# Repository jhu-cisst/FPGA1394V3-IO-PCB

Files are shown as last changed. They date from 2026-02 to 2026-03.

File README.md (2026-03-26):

# FPGA1394V3-IO-PCB

PCB design for I/O board used with [FPGA1394V3](https://github.com/jhu-cisst/FPGA1394V3), in KiCad format.

This board connects to the DF11 connector (J9) on FPGA1394V3, which provides +3.3V, GND and 4 I/O signals (MIO34-37) from the Zynq SoC PS, and makes protected versions of these signals available on a DB9F connector. Specifically, the +3.3V output has a 100 mA current limit and the I/O signals have 50 Ohm current-limiting resistors and a transorb (TVS diode) for protection.

This board is used in the [dVRK Si Controller](https://github.com/jhu-dvrk/dVRK-Si-Controller), starting with Rev 4 of the enclosure.

## DB9F Connector Pinout

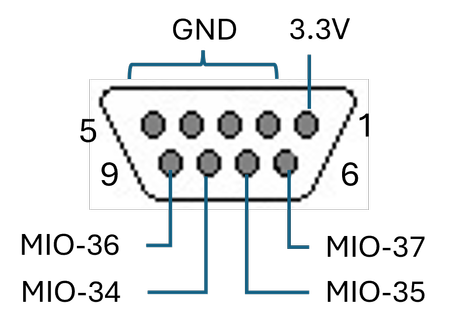
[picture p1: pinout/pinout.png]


## Files

* `dvrk-ios.kicad_pro`: KiCad project file
* `dvrk-ios.kicad_sch`: Schematics (KiCad format)
* `dvrk-ios.kicad_pcb`: PCB layout (KiCad format)
* `dvrk-ios-bom.xlsx`: Bill of Materials (Excel format)

## Subdirectories
(These are not required, since the symbols and footprints are already stored in the kicad_sch and kicad_pcb files)

* `3d`: 3D models of parts
* `DVRK.pretty`: Library of footprints (for PCB)
* `symbols`: Library of symbols (for schematics)

## Release Assets

* `dvrk-ios-schematics.pdf`: Schematics
* `dvrk-ios-pcb.zip`: Gerber files for PCB fabrication
* `dvrk-ios-assembly.zip`: Assembly files (BOM, CPL) for JLCPCB

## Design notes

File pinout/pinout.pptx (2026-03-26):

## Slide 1

3.3V

GND

5

1

9

6

MIO-36

MIO-34

MIO-37

MIO-35

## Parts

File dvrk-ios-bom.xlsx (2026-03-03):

 | FPGA1394V3 I/O Board, Rev 1
 | Bill Of Materials
 | 2026-03-02
Seq | Qty. | Ref Des | Description | Package | Manufacturer | Notes | Manufacturer Part # | Digikey Part # | JLCPCB Part #
1 | 1 | C1 | CAP, 1uF, 10%, 16V, X7R, 0603 | 0603 | TDK | 1 | C1608X7R1C105KT000N | 445-1604-1-ND | C59782
2 | 2 | C2-3 | CAP, 10uF, 20%, 16V, 0603 | 0603 | Murata | 1 | GRM188C81C106MA73D | 490-7198-1-ND | C182375
3 | 1 | C4 | CAP, 0.1uF, 10%, 16V, X7R, 0603 | 0603 | Kemet | 1 | C0603C104K4RACTU | 399-C0603C104K4RACTUCT-ND | C2181816
4 | 1 | D1 | LED, Red, 0805 | 0805 | Generic | 2 |  |  | C2295
5 | 1 | J1 | CONN, RA, DB9 Female, 0.318", 4-40 Screwlock | DB9F | EDAC | 1 | 622-009-260-033 | 151-622-009-260-033-ND | C75749
6 | 1 | J2 | CONN, RA, DF-11, 6-pin | DF-11-6-RA | Hirose |  | DF11-6DP-2DS(24) | H10245-ND | C506666
7 | 4 | R1-4 | RES, 50 Ohm, 1%, 1/8W, 0603 | 0603 | Vishay Dale | 1 | CRCW060350R0FKEA | 541-3318-1-ND | C844932
8 | 1 | R5 | RES, 499 Ohm, 1%, 1/10W, 0603 | 0603 | Generic | 1 |  |  | C103675
9 | 1 | U1 | IC, Power Switch, 100 mA | SOT-23-5 | Microchip |  | MIC2091-1YM5-TR | 576-3891-1-ND | C148025
10 | 1 | U2 | IC, TVS Diode Array, 3.3V | SOT-23-6 | Semtech |  | SMS3.3.TCT | SMS3.3.TCTCT-ND | C780132
11 | 1 |  | PCB, FPGA1394V3-IO (dVRK Aux I/O), Rev 1
Notes:
 | ● | Unless specified otherwise, the only substitutions allowed are substituting identical part number parts from a different manufacturer.
 | 1 | Any component in an identical package that meets or exceeds all the parameters specified in the description can be substituted.
 | 2 | Yellow color may be substituted (JLCPCB #C2296)

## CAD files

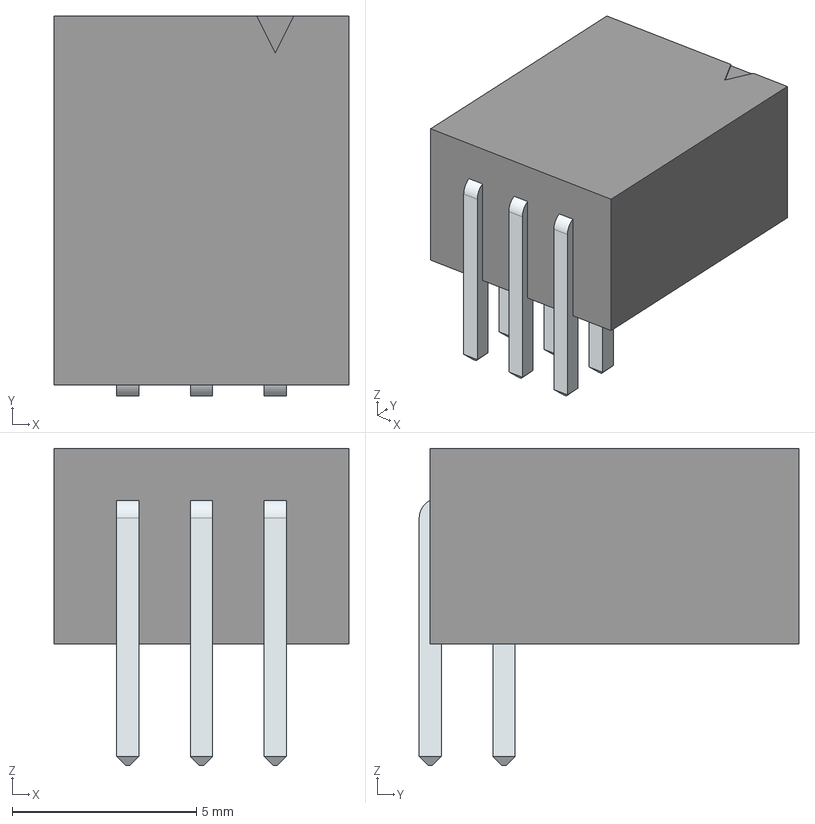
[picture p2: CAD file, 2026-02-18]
3d/DF11-6DP-2DS_24_.stp
8.00 x 10.3 x 8.60 mm
LeadsArray x 2

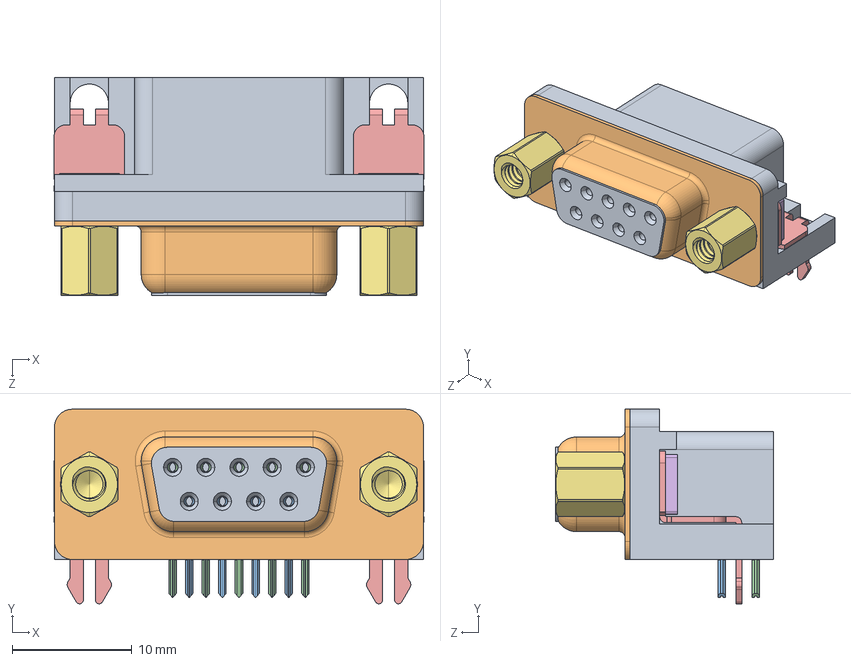
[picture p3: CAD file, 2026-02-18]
3d/622-009-260-033 - EDAC D-Sub Connector.STEP
30.9 x 16.2 x 18.2 mm
622 Housing_9 Socket
622 Shell_9 Socket
622 Socket Bottom x 4
622 Contact Top x 5
622 2 Prong Board Lock x 2
622 4-40 Threaded Rivet x 2
622 4-40 Hex Standoff 5 x 2

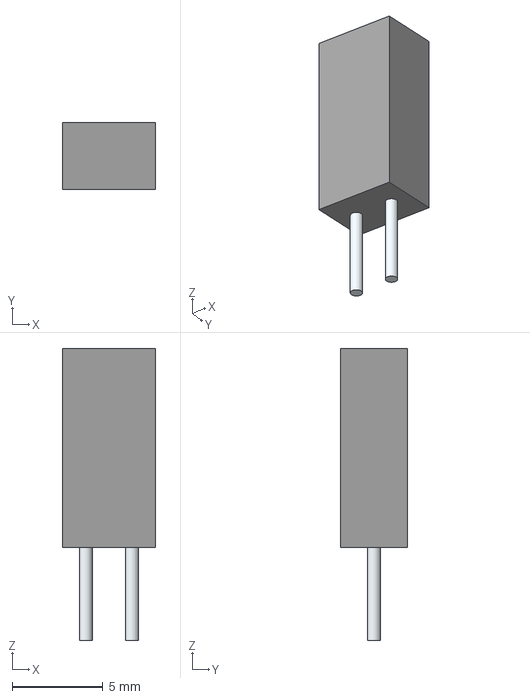
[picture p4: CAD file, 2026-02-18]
3d/C5SMF-RJF-CT0W0BB2.stp
5.10 x 3.70 x 16.0 mm
Leads

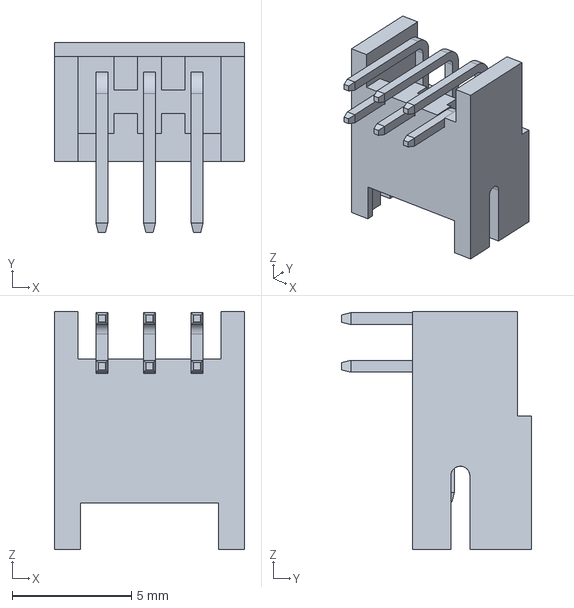
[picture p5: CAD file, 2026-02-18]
3d/DF11-6DP-2DS.stp
8.00 x 8.00 x 10.0 mm

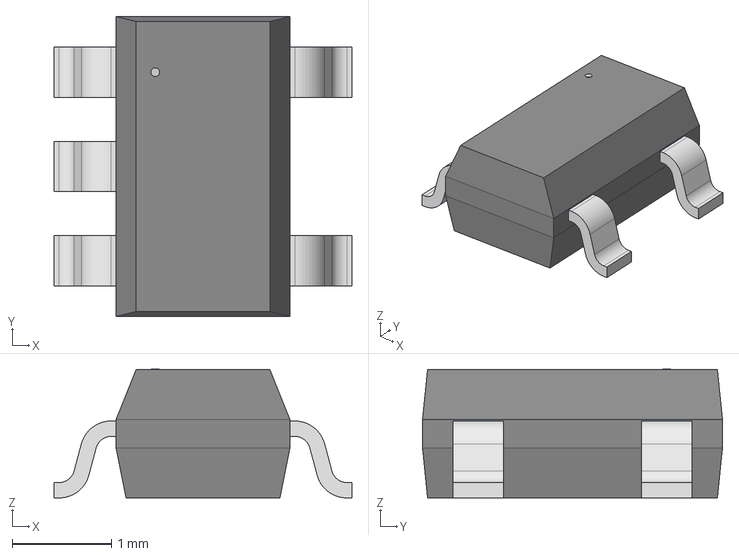
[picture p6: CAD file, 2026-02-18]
3d/SOT-23-5_M5_MCH.step
3.00 x 3.02 x 1.30 mm

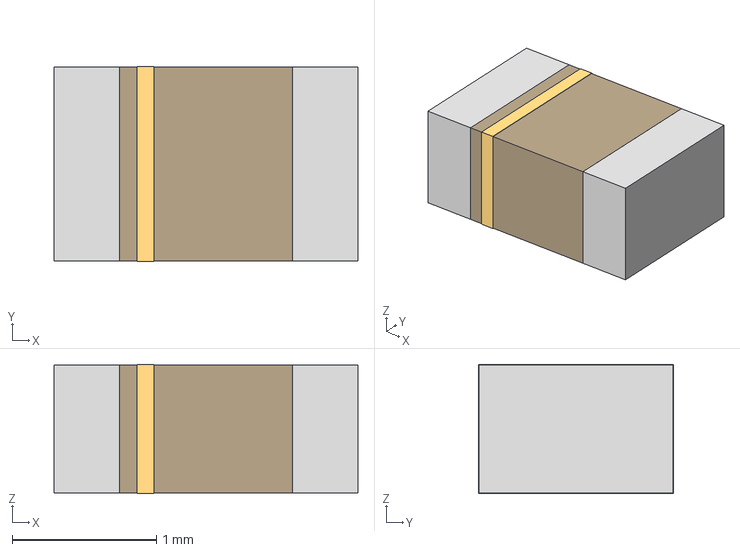
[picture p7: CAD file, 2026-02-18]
3d/LED_LSM0805-2P0X1P25X0P8_VCC.step
2.11 x 1.35 x 0.895 mm

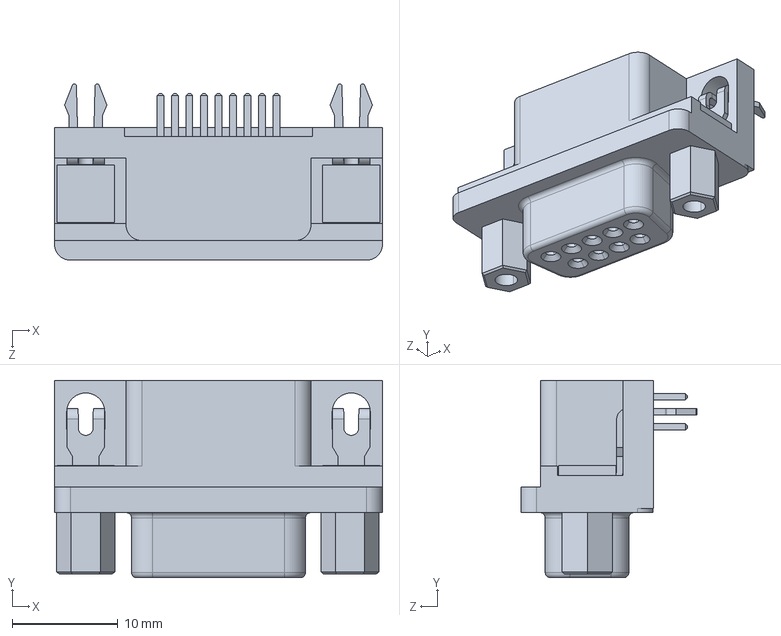
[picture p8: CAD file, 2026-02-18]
3d/6E17C009SBF220.stp
31.0 x 18.6 x 16.7 mm

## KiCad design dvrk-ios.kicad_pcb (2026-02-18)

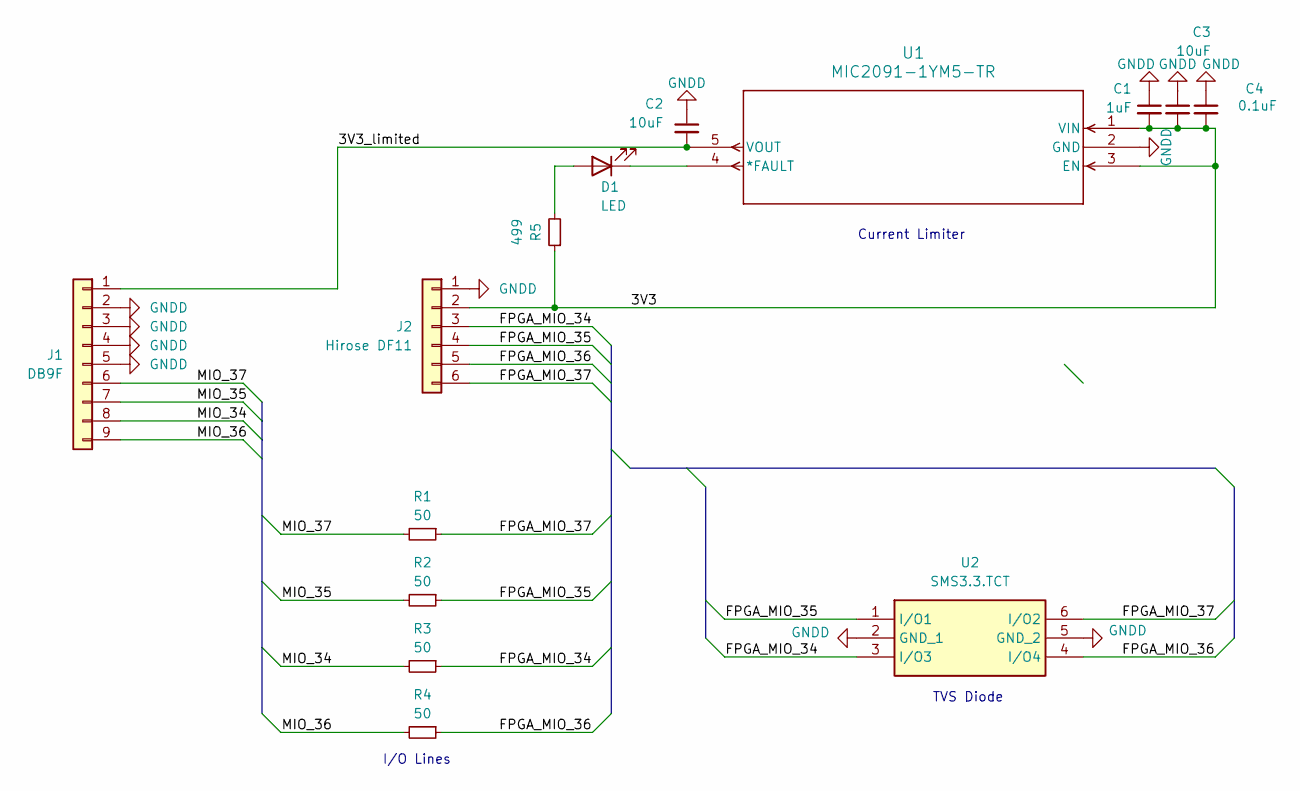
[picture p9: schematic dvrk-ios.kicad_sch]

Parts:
C1: 1uF; C_0603_1608Metric
C2, C3: 10uF; C_0603_1608Metric
C4: 0.1uF; C_0603_1608Metric
D1: LED; LED_LSM0805-2P0X1P25X0P8_VCC
J1: DB9F; 6E17C009SBF220
J2: Hirose DF11; SHDRRA6W60P200X200_2X3_800X1000X530P
R1, R2, R3, R4: 50; R_0603_1608Metric
R5: 499; R_0603_1608Metric
U1: MIC2091-1YM5-TR; SOT-23-5_M5_MCH
U2: SMS3.3.TCT; SOT95P280X145-6N; Mouser Part Number 947-SMS3.3.TCT

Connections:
/3V3: C1.2, C3.2, C4.2, J2.2, R5.1, U1.1 (VIN), U1.3 (EN)
/3V3_limited: C2.2, J1.1, U1.5 (VOUT)
/FPGA_MIO_34: J2.3, R3.1, U2.3 (I/O3)
/FPGA_MIO_35: J2.4, R2.1, U2.1 (I/O1)
/FPGA_MIO_36: J2.5, R4.1, U2.4 (I/O4)
/FPGA_MIO_37: J2.6, R1.1, U2.6 (I/O2)
/MIO_34: J1.8, R3.2
/MIO_35: J1.7, R2.2
/MIO_36: J1.9, R4.2
/MIO_37: J1.6, R1.2
GNDD: C1.1, C2.1, C3.1, C4.1, J1.2, J1.3, J1.4, J1.5, J2.1, U1.2 (GND), U2.2 (GND_1), U2.5 (GND_2)
unnamed: D1.2 (A), R5.2
unnamed: D1.1 (K), U1.4 (*FAULT)

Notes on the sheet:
I/O Lines
Current Limiter
TVS Diode

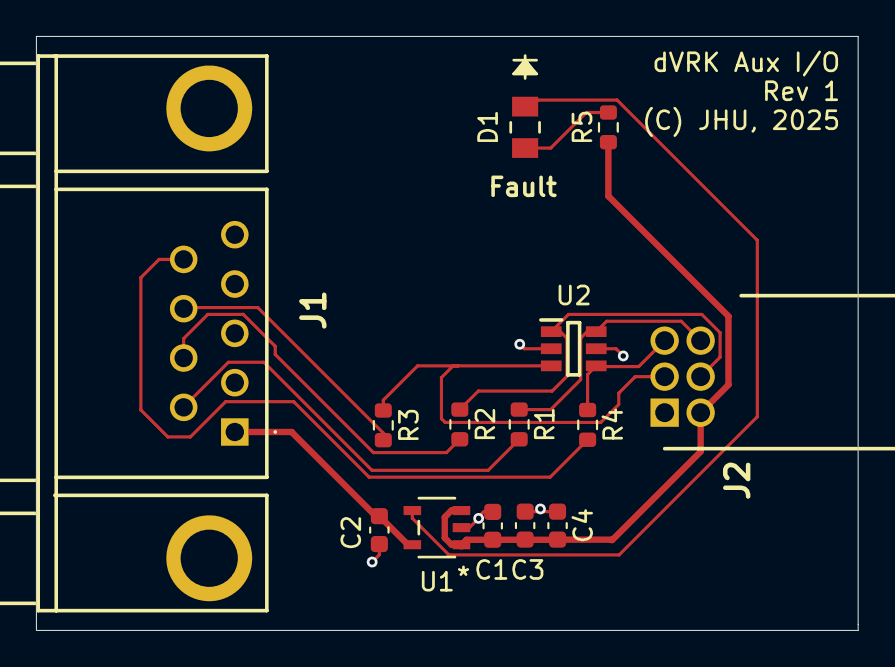
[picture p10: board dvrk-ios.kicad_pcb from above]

Board: 2 copper layers, 45.7 x 33.0 mm, 14 parts (0 on the bottom side), 13 nets.

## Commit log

2026-02-10 Added BOM (Excel format)
    [dvrk-ios-bom.xlsx]
2026-02-18 uploading updated files
    [622-009-260-033 - EDAC D-Sub Connector.STEP, 6E17C009SBF220.stp, C5SMF-RJF-CT0W0BB2.stp, DF11-6DP-2DS.stp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]
2026-02-18 Added Excel BOM (had inadvertently been deleted)
    [dvrk-ios-bom.xlsx]
2026-03-03 Removed production files from repository (move to Release Assets); BOM updates
    [dvrk-ios-B_Cu.gbl, dvrk-ios-B_Mask.gbs, dvrk-ios-B_Paste.gbp, dvrk-ios-B_Silkscreen.gbo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]
